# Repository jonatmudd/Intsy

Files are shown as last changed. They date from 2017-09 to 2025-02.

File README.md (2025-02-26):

# Intsy
32/64/128 channel bioamplifier system, now with accelerometer and on-board SD data logging capability for ambulatory applications! Photos of the original 32/64 channel device are below Also, check out the quick overview of the device internals and mechanical enclosure of the 128 channel ambulatory system in <a href =  "https://www.youtube.com/watch?v=RvYDtEdVOBU&feature=youtu.be">this video</a> (full credit to Riwaj Shrestha, Suyash Mathema, and Jeremy Wharton!).

Intsy is a validated, low-cost, open-source, wireless-enabled bioamplifier system.  The system can be configured for 32, 64, or 128 channel operation.  It has been validated for acquiring high-quality gastrointesinal slow wave and surface EMG electrical signals.  For more details, see our <a href =  "http://iopscience.iop.org/article/10.1088/1361-6579/aaad51">published peer-reviewed article in Physiological Measurement</a>. We have also regularly used Intsy to make <a href = "https://ieeexplore.ieee.org/abstract/document/8839813"> body surface recordings of colonic motilty patterns</a> using  conventiona wet (gel) as well as dry electrodes (see <a  href = "https://link.springer.com/article/10.1007/s10439-023-03137-w"> this journal article  </a>) 

Data can be streamed either in wired configuration over USB or wirelessly via bluetooth.  A LabView GUI allows for real-time visualization and saving to hard disk for off-line analysis.  Data rates of 32 chan x 110 Hz can be stably transmitted over bluetooth.  The USB wired configuration can achieve up to 2 kHz x 128 chan.  Matlab functions for converting binary Intsy data files into matlab format are provided.

The name Intsy comes from the two core components: Intan RHD2132 bioamplifier chip + Teensy 3.6 microcontroller.

Please see "Intsy_Setup_Guide.pdf" for detailed instructions on how to set up the 32/64 channel Intsy system. Assembly time is typically about 4 hrs.  Total cost is about $1500 for the 32 channel system,  $2400 for the 64 channel system, and $6000 for the 128 channel system (the dominant cost being the Intan RHD2132 amplifier boards).  That means  you can build your very own high-quality, low-cost, portable bioamplifier system in just a single afternoon!

All feedback and suggestions are warmly welcomed. 

<p align="center">
  
</p>
Above: Intsy 128 channel electronics and mechanical enclosure (circa May 2020)

<p align="center">
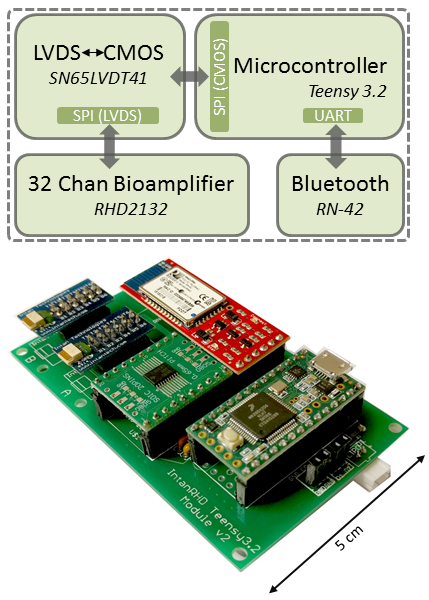
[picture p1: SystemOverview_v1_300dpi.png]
  
</p>
Above: Intsy hardware architecture and device (32/64 channel original module circa Dec 2017)

<p align="center">
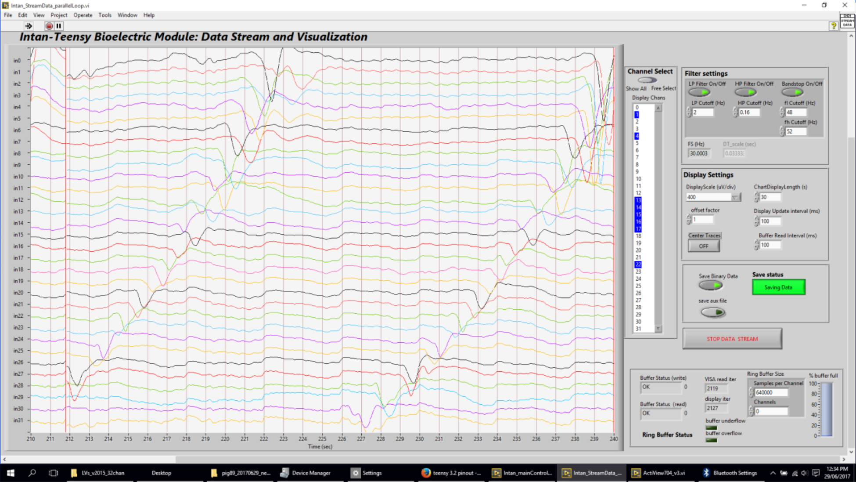
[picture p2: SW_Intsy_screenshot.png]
  
</p>
Above: Screenshot of Intsy Labview front end to visualize and stream signals in real time. The figure shows propagating gastric slow waves.

<p><font size="16"><b>Disclaimer</b></font></p>
The Intsy electronics module is not a medical device nor is it intended for medical diagnosis and provided to you "as is," and we make no express or implied warranties whatsoever with respect to its functionality, operability, or use, including, without limitation, any implied warranties, fitness for a particular purpose, or infringement. We expressly disclaim any liability whatsoever for any direct, indirect, consequential, incidental or special damages, including, without limitation, lost revenues, lost profits, losses resulting from business interruption or loss of data, regardless of the form of action or legal theory under which the liability may be asserted, even if advised of the possibility of such damages. This bioamplifier module does not fall within the scope of the European Union directives regarding electromagnetic compatibility, restricted substances (RoHS), recycling (WEEE), FCC, CE or UL, and therefore may not meet the technical requirements of these directives or other related directives

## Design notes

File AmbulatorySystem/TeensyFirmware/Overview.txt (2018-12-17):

Here you will find firmware for Teensy 3.6.  Compile and upload to Teensy 3.6 board using Arduino IDE
The main file is Intan_ambulatory_20181216.ino.  Opening it in Arduino should open a bunch of tabs with other .ino and .h files
Note: you will also need Bill Greimans' sdfat library before compiling: https://github.com/greiman/SdFat

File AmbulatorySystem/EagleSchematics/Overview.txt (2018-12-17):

Here you will find eagle schematics for the ambulatory board. Gerber files are included. Components mount on front and back
I used 4pcb (Advanced Circuits) to fab my boards.  Seeed studio is another good option I have used before.

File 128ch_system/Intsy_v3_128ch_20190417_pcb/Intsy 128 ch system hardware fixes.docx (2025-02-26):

Intsy 128 ch system hardware fixes. – Compiled 07 July 2019 JE

The system is verified complete and working as of June 2019. However, several fixes had to be made to schematic/board:

1. BT power switch. Connect/solder bridge the 2 pins on the ground line. This ensures BT ground pin and system ground supplied by Teensy are *always* connected. This prevents floating voltages from causing spurious signals in Rx/Tx lines which are always connected between BT and Teensy 3.6.
2. CS pin name/numbers are swapped. This problem is easily sorted by configuring firmware with proper numbers, but better is to fix CS A/B and CS C/D naming convention. They are inadvertently swapped in schematic moving from Intan RHD2000 across the LVDS converter to Teensy.

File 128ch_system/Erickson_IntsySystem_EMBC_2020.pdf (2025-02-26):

## Open-source 128-channel bioamplifier module for ambulatory monitoring of gastrointestinal electrical activity

Jonathan C. Erickson∗
, Beth Reed, Jeremy Wharton, Utkrist Thapa, Jack Robey, and Riwaj Shrestha

Abstract— We present an open-source, low-cost, portable, 128-channel bioamplifier module designed specifically for ambulatory, long-term (≥24 hr) monitoring of gastrointestinal (GI) electrical activity. The electronics hardware integrates stateof-the-art, commercial-off-the-shelf components on a custom PCB. Features include on-board data logging, wireless data streaming, subject motion monitoring, and stable operation up to the maximum 2 kHz/channel sampling rate tested. The new device operates for ≈ 30 hr continuously powered by a single

### 3.7 V, 2500 mAh LiPo battery. The 3D-printed ABS mechanical

enclosure is robust and small (13.1 × 8.8 × 2.5 cm), so that the device can be carried in a standard Holter monitor pouch. Results from initial 128-channel, high spatial resolution body surface colon mapping experiments demonstrate the utility of this new device for GI applications. The new bioamplifier module could also be used for multichannel recording experiments in a variety of biomedical domains to study electrical activity patterns of the neuromuscular system (EMG), uterus (EHG), heart (ECG), and brain (EEG).

I. INTRODUCTION
Multichannel electrical recordings find widespread use in variety of biomedical domains to assess heart (ECG), brain (EEG), neuromuscular (EMG), and uterine (EHG) function. One rapidly growing application area is the gastrointestinal (GI) field. For example, multichannel recordings have recently been used in research and clinical diagnostic settings to map the propagation of gastric slow waves using a minimally invasive endoscopic device as well as a noninvasive cutaneous electrode array [1], [2]. Similarly, electrocolonography (EColG) was recently introduced for noninvasively identifying cyclic motor patterns in the distal colon using an array of skin-surface electrical recordings [3]. As these GI technologies continue to mature, their capability to identify meaningful physiological information may be improved and extended by making recordings with increased spatial density and/or area coverage over a longer multi-day (≥ 24 hr) monitoring period.
To this end, we have developed a novel low-cost, open source, portable device with 128 input channels and on-board data logging capability. The new device, coined “Intsy-128”, is a substantial upgrade over the 32/64-channel electronics module previously developed in our lab, which was validated for making high-quality GI signal recordings [3], [4]. Specific new and upgraded features include: the maximum channel count has been increased from 64 to 128 channels; on-board microSD card data logging has been added to enable ambulatory applications; an accelerometer plus a flex

∗ Corresponding author: ericksonj@wlu.edu. The authors are with the Department of Physics and Engineering, Washington and Lee University, Lexington, VA 24450 USA.

sensor have been added to monitor participant movement; and a more powerful microcontroller has been integrated to support higher sampling rates. Additionally, we developed a small footprint, robust, custom 3D-printed ABS enclosure for the electronics board, which makes the new Intsy-128 device well suited for portable, ambulatory applications. The remainder of this paper details the electronic and mechanical design of the new Intsy-128 module. Herein, we also demonstrate the utility of this device in the GI field through initial experiments mapping colonic cyclical motor patterns stimulated by food intake using recordings from a 128-channel body surface electrode array. While the Intsy-128 was developed specifically with GI applications in mind, it could also be used in multichannel recording applications to study cardiac, neural, musculoskeletal, and uterine electrical activity patterns (e.g. [5]).

II. MATERIALS AND METHODS

A. Electronics Hardware System Design
The Intsy-128 electronics hardware is comprised of six main components integrated on a custom PCB (Figure 1 a-b). These include: Teensy 3.6 microcontroller (PJRC; Sherwood, OR); four Intan RHD2132 amplifier boards (Intan Technologies; Los Angeles, CA), two Texas Instruments SN65LVDT41 LVDS-CMOS transceivers for SPI over LVDS; one ADXL335 3-axis accelerometer (Adafruit Industries; New York City, NY) and a RN-42 “SilverMate” Bluetooth modem (Sparkfun; Niwot, CO). The custom PCB was designed using the free version of Eagle PCB design software (version 9.4). The module can be easily assembled in about 4 hrs using basic through-hole and surface mount soldering techniques.
The Teensy 3.6 microcontroller was selected because it offers multiple SPI ports; a relatively fast and powerful CPU (180 MHz ARM Cortex-M4); and native microSD support via a 4-bit SDIO interface with a maximum 12 MB/s write speed. On-board data logging is required for ambulatory studies. Each of four Intan RHD2132 amplifier boards has 32 inputs for a total of 128. The amplifier boards are interfaced to two SPI ports on the Teensy 3.6. The TI SN65LVDT41 ICs are used to translate TTL/CMOS signals used by Teensy 3.6 to low-voltage differential signaling (LVDS) used by the Intan headstages.
The RN-42 wirelessly streams data to a host PC for real-time signal visualization and analysis. RTS/CTS flow control was enabled for robust data transfer. Additionally, the Teensy firmware configures the wireless data stream to transfer the maximum possible number of channels at full

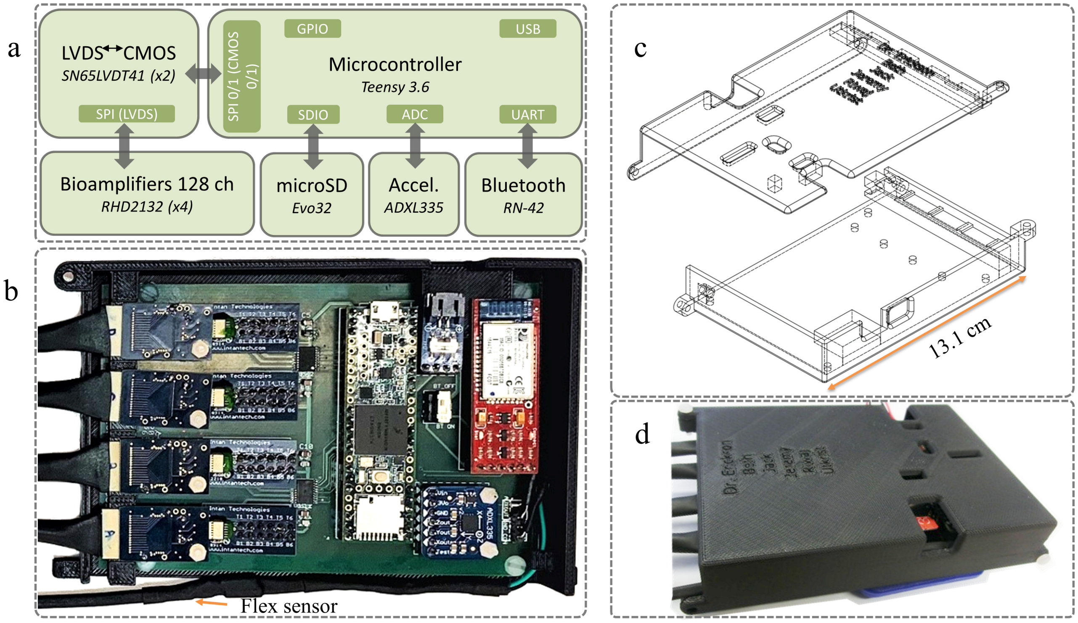
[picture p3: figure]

Fig. 1. System overview of the Intsy 128 device. a: Electronics design block diagram; b: Fully assembled PCB mounted in base of enclosure; c: 3-D CAD rendering of enclosure assembly showing base and lid. d: Fully assembled Intsy-128 module.

sampling rate without exceeding the total Bluetooth bandwidth. Alternatively, data may be streamed in real-time over
the USB port for higher bandwidth applications. Independent of data streaming, all data bytes are always logged on-board to a microSDHC UHS-I memory card (Samsung EVO Plus 32GB). Data logging write-speed was optimized by preallocating the data file and writing 512-byte (1-page) blocks to the microSD card data file. Each data frame consists of 270 bytes, including 256 bytes for electrical recordings (2-bytes for each of 128 amplifiers), 4-byte microsecond timestamp, and 10 bytes of “magic number” synchronization characters used to verify fidelity of SPI and SDIO interfaces.
The 3-axis accelerometer (ADXL335) and a custom flex sensor are used to measure subject motion during the study. The flex sensor is configured as a standard voltage divider comprised of a 47kΩ fixed resistor in series with a approx 20-400kΩ flexible resistor (Sparkfun) and is powered by a 3.3 V digital output pin on the Teensy 3.6. The accelerometer readings could be used for analysis of multi-day ambulatory monitoring applications [6]. Similarly, the flex sensor is more sensitive to subtle motions, such as bending or twisting of the abdomen, and may be used in the future to improve automated artifact reduction techniques [7].
The Insty-128 module is powered by a 3.7 V, 2500 mAh LiPo flat pack battery with an easily accessible switch to turn the device on or off. A separate power switch independently controls the Bluetooth module allowing users to save battery power when real-time wireless streaming is not required.

LED indicator lights on both the Bluetooth module and Teensy 3.6 serve as system status indicators.

B. 3D-Printed Enclosure

The electronics hardware module is secured inside a custom 3D-printed ABS enclosure case, which is durable and protects internal hardware from mechanical impacts experienced during an ambulatory subject experiment. The enclosure consists of a base and lid (Figure 1c). Seven nylon nuts and bolts secure the PCB circuit board and the lid onto the base of the case providing quick and efficient assembly (Figure 1d).
A wide-tooth “comb” pattern of indentations (15 mm wide with 2.5 mm gaps) was carefully incorporated into the base and lid to secure the connection between the electrodes and the amplifiers. Additionally, multiple ports are provided for viewing status-indicator LEDs, toggling power switches, and conveniently accessing the microSD card and USB port. The design focused on making a light and slim device conducive for ambulatory studies. The case dimensions are 13.1 × 8.8 × 2.5 cm, approximately the same size as a typical Holter cardiac monitor; thus, it can be easily carried in a Holter monitor pouch. The Intsy-128 module weighs a total of 216 grams, including the the fully-assembled PCB, ABS enclosure, and LiPo battery mounted externally on the enclosure’s base in a vinyl cell phone wallet pouch.

C. Software User Interface
A user-friendly custom suite of software built in Labview 2017 (National Instruments; Austin, TX) was used for device configuration and visualizing signals in real-time. This interface allows the user to configure the sampling rate, band-pass filter cutoffs for the Intan RHD2132, and SD card log file name. The LabView interface is also used to configure and optionally apply digital filters, as well as select a subset of channels, prior to display.
A file reader utility developed in Matlab 2019a (The Mathworks Inc; Nattick, MA) was used to import and convert the raw binary data files into physical values for further analysis. Firmware for the Teensy 3.6 was programmed using Teensyduino [8] in the Arduino IDE. All custom software, PCB and CAD design files are freely available and fully open-source [9].
D. Meal-response experiment
To demonstrate the utility of the Intsy-128 device, we performed initial body surface colon mapping experiments with n = 5 human subjects, following the protocol described in [3]. This study was approved by the Institutional Review Board of Washington and Lee University. In this study, we placed a 128-channel electrode array on the lower abdomen toward lower subject’s left side, approximately covering the sigmoid and descending colon. The 128-channel array was formed using two 64-channel (8 × 8) grids with 10 mm spacing (OTbioelettronica; Torina, Italy). We recorded signals for ≈90 min in the fasted state, and another 90 min in the fed state. The sampling rate was set to 100 Hz. Colonic signal analysis was based on the Continuous Wavelet Transform (CWT) [3]. Additionally, we quantified the acceleration magnitude as: A =

q
a

2
x + a

2
y + a

2
z

III. RESULTS

A. Hardware Performance Benchmark
Data logging was accurate and robust; zero errors were observed during approximately 60 hours of hardware validation experiments. The device remains stable at sampling rates up to 2000 Hz, the highest sampling frequency tested. The total current draw was measured be ≈100 mA; the LiPo battery continuously powered the module for ≈ 30 hr before it needed to be recharged. Users reported the device was unobtrusive and comfortable to wear over the duration of a 3-4 hr study.
B. Proof of Concept GI recordings
The Intsy-128 device made high-quality recordings of bioelectric activity. Figure 2 illustrates representative results for the body surface colon mapping experiments from one test subject. We visually assessed the ECG waveform (digitally high-pass filtered, 1 Hz cutoff) with the QRS complex and T-wave clearly visible as a proxy indicator for good-quality, low impedance electrode-skin contact (Fig. 2a). The EColG time-domain signal (digitally band-pass filtered, 0.5-10 cpm) indicates a clear increase in colonic activity at a dominant frequency of 3.2 cylces per minute (cpm) in the fed vs. the fasted state (Fig. 2b). CWT spectral analysis shows the time-course of increased colonic activity following meal-ingestion (Fig. 2c). Note that the time-course of increased subject motion during eating (acceleration A low-pass filtered at 1 Hz, gray trace), does not explain a proportionally much larger rise in post-meal colonic activity (Fig. 2d). The time-course of increased post-meal colonic activity beginning about 12 min after eating and lasting for about 30 min is strongly concordant with the cyclic motor activity in the distal colon previously characterized [3], [10]. Fig. 2e shows the 128-channel electrode array placed on the lower abdominal surface below umbilicus (overhead view). The flex sensor is visible as finger-like projection on the left-side of the photo (subject’s right). The overlaid black curves indicate the approximate location and orientation of a segment of the colon identified from body surface mapping localization. The body surface heat map computed from the power-percent difference in pre- vs. post-meal activity [3] localizes the active colonic regions to the infraumbilical region, toward the left iliac crest (Fig. 2f). The velocity field map (Fig. 2g) was derived using the surface Laplacian and phase-based analysis
[11] indicates retrograde wave activity originating near the rectosigmoid region propagating at of 5.3 ± 2.0 mm/s (mean ± s.d.), in reasonable accord with findings from previous high-resolution manometry studies [10].

IV. DISCUSSION

A. Comparison to other modules
The new Intsy-128 device is a low cost, open-source, easy to assemble bioamplifier module well-suited for ambulatory bioelectrical signal acquisition and analysis. Table I compares Intsy-128 to similar and academically-sourced and open-sourced hardware. Intsy-128 offers the highest channel count and sampling frequency compared to other devices in its class. The on-board data logging capability and motion monitoring make it especially well-suited for ambulatory studies. The Intsy-128 may be an attractive option for budget-conscious labs, fostering new discovery and innovation throughout the scientific community.
| Intsy-128 | Ref [12] | OpenBCI [13]
Number channels | 128 | 64 | 16
Resolution (bits, µV/bit) | 16, 0.195 | 10, 1.56 | 24, 0.006
Dynamic Range (mV) | ±5 | ±3 | ±104
Analog filter | 0.02 Hz-5kHz | 0.016-1.6 Hz | no filter
Max Sampling Rate (kS/s) | 256 | 64 | 16
Validation in vivo | Yes | No | Yes
Cost/channel (USD) | 35 | unknown | 59

TABLE I

COMPARISON OF AMBULATORY-READY SYSTEMS.

B. Potential applications and future work
In the future, the size and cost of the Intsy-128 module could be optimized by combining all individual components on a single custom PCB using all surface mount assembly, as opposed to mounting relatively large submodules with through-hole soldering. The addition of WiFi capability would allow for higher bandwidth streaming, which is important for applications with much higher sampling frequencies (≥ 500 Hz), as are typical in the neural and cardiac fields.
V. CONCLUSIONS
We have developed a novel low-cost, open-source, 128-channel bioamplifier module, suitable for ambulatory studies. Results from ≈3 hr colonic meal response study conducted in a laboratory setting demonstrate its potential use in high-resolution mapping studies of GI electrical activity patterns. In the future, it can also be used for longer-term monitoring and diagnostic studies. The Intsy-128 bioamplifier module could also be used to study electrical activity patterns of the brain, heart, skeletal muscle, and uterus.

VI. ACKNOWLEDGMENT
This work was supported by the Washington and Lee University Lenfest Faculty Research Grant (JCE); Advanced Immersion and Mentoring Program (JW); Allen Research Grant (JR); and Summer Research Scholars Program (UT and RS).

REFERENCES

[1] T. Angeli et al., “High-resolution electrical mapping of porcine gastric slow-wave propagation from the mucosal surface,” Neurogastroenterology & Motility, vol. 29, no. 5, 2017.
[2] A. A. Gharibans et al., “Spatial patterns from high-resolution electrogastrography correlate with severity of symptoms in patients with functional dyspepsia and gastroparesis,” Clinical Gastroenterology and Hepatology, 2019.
[3] J. C. Erickson et al., “Electrocolonography: Non-invasive detection of colonic cyclic motor activity from multielectrode body surface recordings,” IEEE Transactions on Biomedical Engineering, 2019.
[4] ——, “Intsy: a low-cost, open-source, wireless multi-channel bioamplifier system,” Physiological measurement, vol. 39, no. 3, p. 035008, 2018.
[5] C. Rabotti and M. Mischi, “Propagation of electrical activity in uterine muscle during pregnancy: a review,” Acta Physiologica, vol. 213, no. 2, pp. 406–416, 2015.
[6] N. Paskaranandavadivel et al., “Multi-day, multi-sensor ambulatory monitoring of gastric electrical activity,” Physiological measurement, vol. 40, no. 2, p. 025011, 2019.
[7] A. A. Gharibans et al., “Artifact rejection methodology enables continuous, noninvasive measurement of gastric myoelectric activity in ambulatory subjects,” Scientific reports, vol. 8, no. 1, p. 5019, 2018.
[8] P. Stoffregen, “Teensyduino: a software add-on for the arduino,” https: //www.pjrc.com/teensy/teensyduino.html, accessed: 2020-01-25.
[9] “Github: Intsy 128-channel ambulatory bioamplifier system,” https://github.com/jonatmudd/Intsy/tree/master/AmbulatorySystem, accessed: 2020-01-30.
[10] P. Dinning et al., “Quantification of in vivo colonic motor patterns in healthy humans before and after a meal revealed by high-resolution fiber-optic manometry,” Neurogastroenterology & Motility, vol. 26, no. 10, pp. 1443–1457, 2014.
[11] A. A. Gharibans et al., “High-resolution electrogastrogram: A novel, noninvasive method for determining gastric slow-wave direction and speed,” IEEE Transactions on Biomedical Engineering, vol. 64, no. 4, pp. 807–815, 2017.
[12] A. Javan-Khoshkholgh and A. Farajidavar, “An implantable inductive near-field communication system with 64 channels for acquisition of gastrointestinal bioelectrical activity,” Sensors, vol. 19, no. 12, p. 2810, 2019.
[13] “OpenBCI,” https://shop.openbci.com/collections/frontpage/products/cyton-biosensing-board-8-channel?variant=38958638542, (https://shop.openbci.com/collections/frontpage/products/cyton-biosensing-board-8-channel?variant=38958638542) accessed: 2020-01-20.

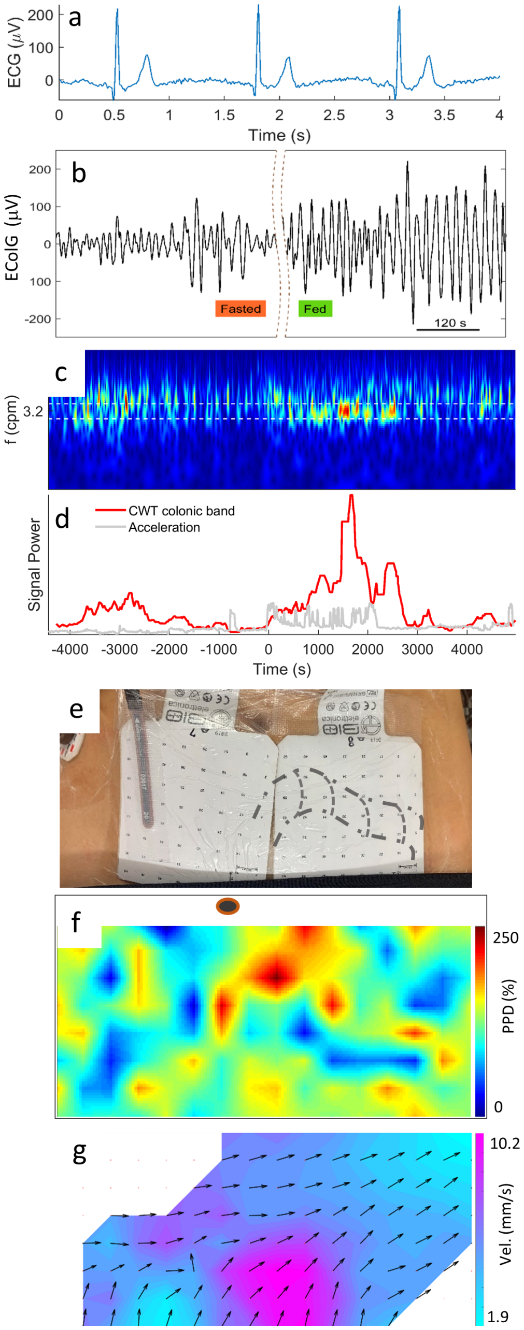
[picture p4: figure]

Fig. 2. EColG meal-response experiment representative results. a: ECG waveform. b: EColG signals in fasted and fed state; note the “broken” time axis. c, d: CWT analysis showing strong post-meal activity with a dominant frequency of 3.2 cpm; e: Photo of electrode array positioned on lower abdomen spanning subject’s midline; f: Heat map localizing colonic post-meal activity. Brown circle denotes belly button position; g: Velocity field map indicating a retrograde motor pattern.

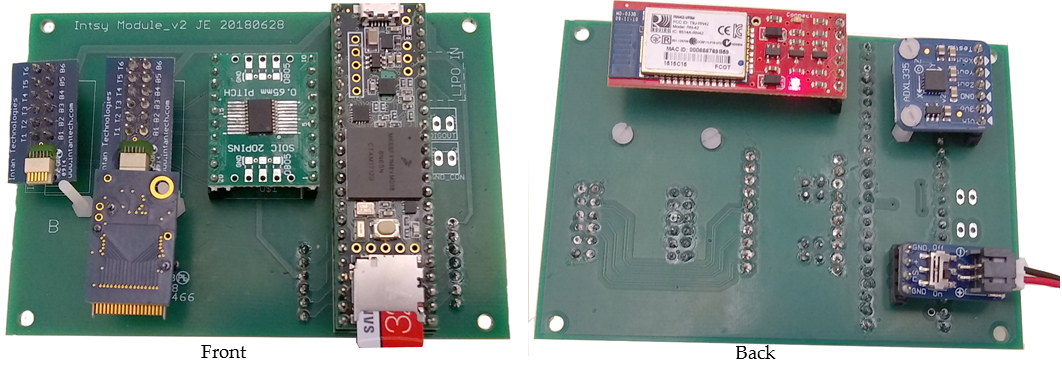
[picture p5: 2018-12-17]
IntsyAmbulatoryFrontBack_cropped_new.png

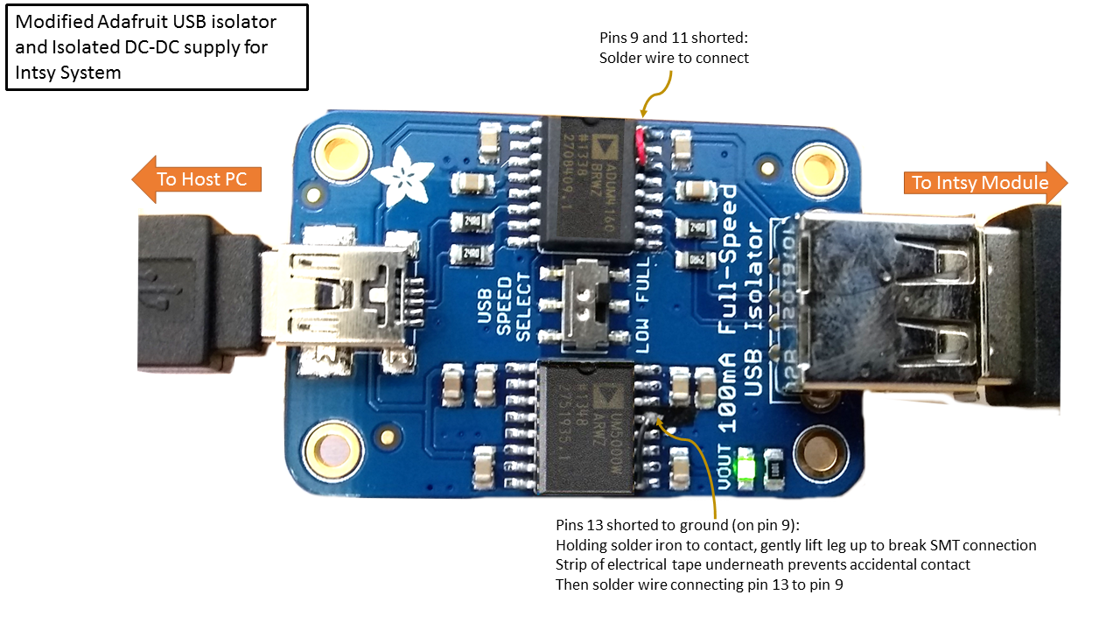
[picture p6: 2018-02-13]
USBisolator_modififcation.png

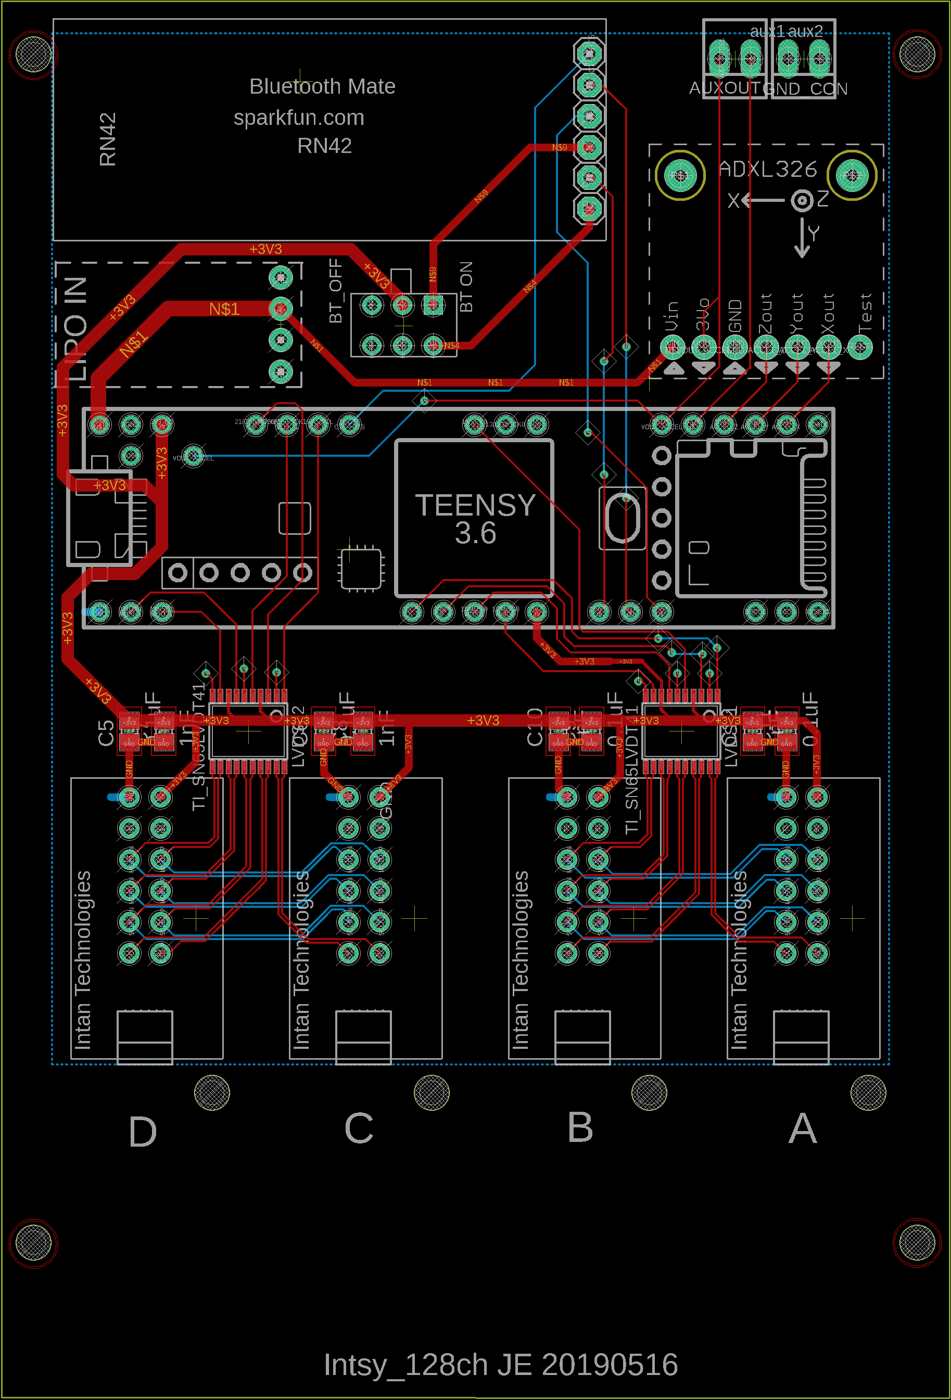
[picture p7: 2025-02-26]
128ch_system/Intsy_v3_128ch_20190417_pcb/Intsy_128ch_highRes.png

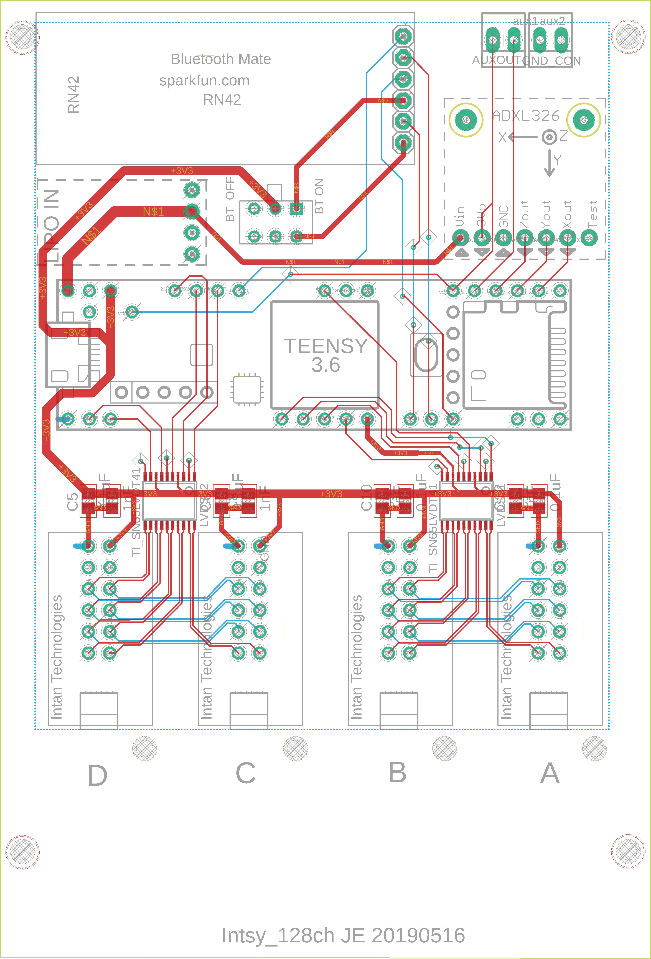
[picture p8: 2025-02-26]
128ch_system/Intsy_v3_128ch_20190417_pcb/Intsy_128ch_1200dpi.png

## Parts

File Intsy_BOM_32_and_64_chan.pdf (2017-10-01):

1

I. BILL OF MATERIALS

TABLE I

BILL OF MATERIALS FOR INTSY BIOAMPLIFIER MODULE. PRICES DO

NOT INCLUDE TAX OR SHIPPING.

Item | Vendor (part #) | Cost (USD)
RHD2132 amplifier board | Intan Tech (C3314) | 895 per 32 chan amp board
SPI cable adapter board | Intan Tech (C3430) | 98 per amp board
36 pin electrode adapter board | Intan Tech (C3420) | 190 per amp board
Teensy 3.2 microcontroller | Adafruit (2756) | 20
RN-42 Bluetooth module Silver mate | Sparkfun (WRL-12576) | 25
TI LVDS-CMOS driver/receiver SN65LVDT41 | Mouser (595-SN65LVDT41PW) | 8
Schmartboard 0.65mm SOIC to DIP adapter | Mouser (872-204-0006-01) | 6
Male and Female 0.1” pitch headers | Adafruit (3009; 3008) | 5
Bypass capacitors, 2 x 0.1 uF, 2 x 1 nF | Mouser (80-C320C104K5R; 75-
| 564R60GAD10) | 1
JST LiPo battery connector | Sparkfun (PRT-08613) | 1
LiPO battery (3.7 V; 1200 mAh) | Adafruit (258) | 10
USB isolator | Adafruit (2107) | 35
Custom PCB | Seeed Studio | 10
TOTAL | | 1304 (32 chan)/2487 (64 chan)

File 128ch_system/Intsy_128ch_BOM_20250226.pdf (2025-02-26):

## Intsy 128 channel bioamplifier module: Bill of Materials

(compiled Jon Erickson Feb 26 2025)

Item | Vendor (part #) | Unit Cost (USD) | Quantity (for 128 ch)
RHD2132 headstage | Intan Tech (C3314) (https://intantech.com/RHD_headstages.html?tabSelect=RHD32ch) | 920 | 4
SPI cable adapter board | Intan Tech (C3430) (https://intantech.com/RHD_SPI_cables.html?tabSelect=RHDSPIadapter) | 111 | 4
36 pin-wire adapter | Intan Tech (C3420) (https://intantech.com/electrode_adapters.html?tabSelect=Wire36pin) | 230 | 4
Teensy 3.6 microcontroller | N/A ¹ | 20 | 1
TI LVDS-CMOS driver receiver SN65LVDT41PW | Mouser (595-SN65LVDT41PW) (https://nz.mouser.com/ProductDetail/Texas-Instruments/SN65LVDT41PW?qs=QViXGNcIEAu2oZm1OztEtQ%3D%3D) | 18 | 2
RN-42 Bluetooth module Silver mate | Sparkfun² (retired part) (https://learn.sparkfun.com/tutorials/using-the-bluesmirf/hardware-overview) | 25 | 1
ADXL335 analog 3-axis accelerometer | Adafruit (163) (https://www.adafruit.com/product/163) | 15 | 1
JST switch | Adafruit (1863) (https://www.adafruit.com/product/1863) | 3 | 1
Bypass caps: 0.1 uF; 1 nF | Mouser (80-C320C104K5R; 75-564R60GAD10) | 4 (of each value) | 1
USB isolator | Adafruit (2107) (https://www.adafruit.com/product/2107) | 35 | 1
LiPo battery (3.7 V; 2500 mAh) ³ | Adafruit (328) (https://www.adafruit.com/product/328) | 15 | 1
Custom PCB | Seeed Studio or Advanced Circuits | 10 | 1
3D printed enclosure | Local 3D printer | ~20 | 1
Nylon screws and nuts (various sizes, eg M2) | McMaster-Carr | 5 | various
Snap leads (0.5 m, 10x pack) ⁴ | OpenBCI (snap leads) (https://shop.openbci.com/products/emg-ecg-snap-electrode-cables?variant=46183825277168) | ~ 600 | 13 packs

1

Teensy 3.6 is now deprecated and common vendors (Digikey, Mouser, Adafruit, Sparkfun, PJRC) appear to be out of stock. If a Teensy 3.6 cannot be procured, one alternative is to use a Teensy 4.1 (blazing fast!). Note: T4.1 is not a drop-in replacement (not pin-for-pin compatible), therefore the pcb files must be updated accordingly!

2 RN-42 Bluetooth silver mate module is now ‘retired’ by sparkfun. Suggested workarounds: 1) Use the Intsy module in wired mode only. In this case, the Bluetooth module is not required and may be entirely left off the board. 2) the RN-42 bluetooth component is still available from various vendors. Buy one of these, then download and fabricate one of sparkfun’s original pcbs for the silver mate module.

3

LiPo battery with 2500 mAh battery should be sufficient for running the Intsy module for approximately ~ 16 hr ( = 2500 mAh/150 mA = 50/3 hr). WARNING: only a single power source may be safely applied to the Intsy module. The LiPo battery and USB cord should should NEVER be plugged in at the same time!

4 Any snap leads will do. OpenBCI offers one relatively inexpensive option. However, in my hands, some of the clips are cheaply made and fail (probably 1 out of 20).

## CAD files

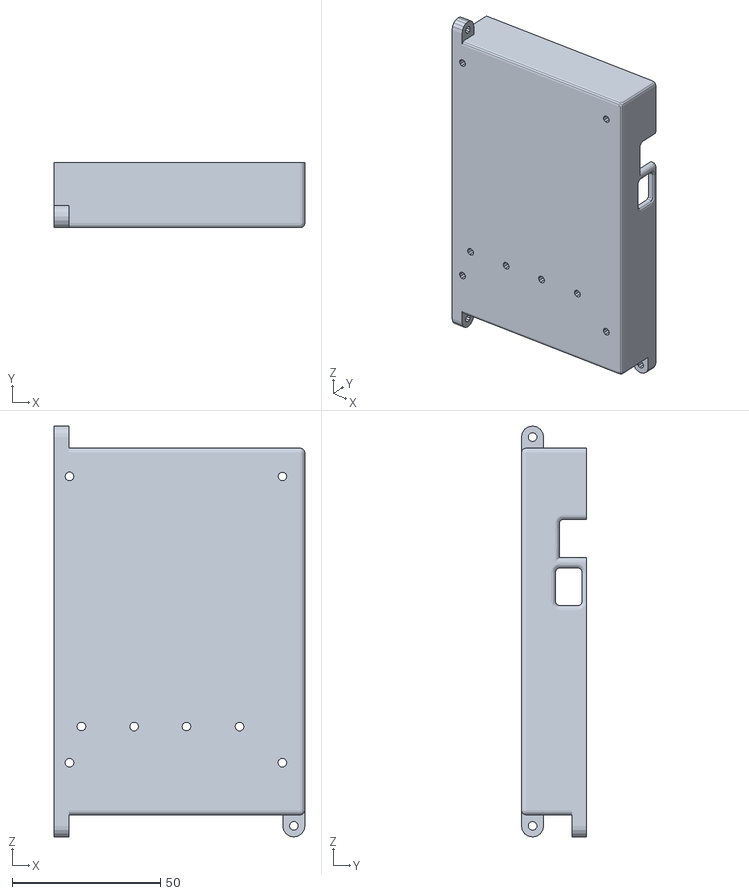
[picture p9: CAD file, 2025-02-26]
128ch_system/Box_128Chan_3dprint/ENGN_128chan_box_4.stl
84.8 x 22.0 x 138.8

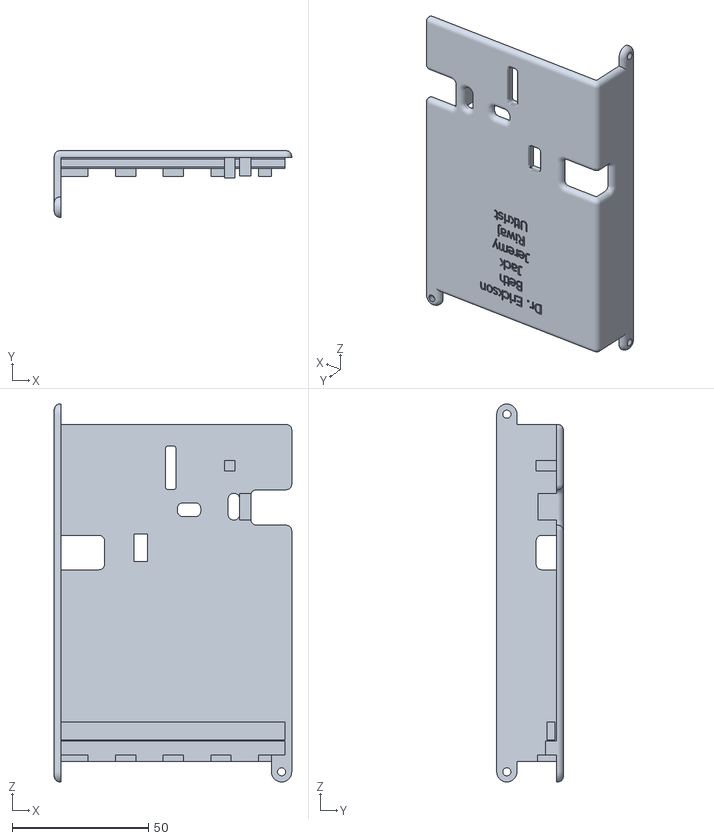
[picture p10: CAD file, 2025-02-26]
128ch_system/Box_128Chan_3dprint/ENGN_128chan_lid_4.stl
87.3 x 24.5 x 138.8

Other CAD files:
128ch_system/Box_128Chan_3dprint/128chan_box_Botton half Drawing.dwg
128ch_system/Box_128Chan_3dprint/128chan_lid.dwg
128ch_system/Box_128Chan_3dprint/128chan_box_2_FixedMeasurements.ipt

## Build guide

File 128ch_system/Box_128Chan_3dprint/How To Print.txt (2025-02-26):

0) If the latest version of the box or lid has been modified,
	it will have to be exported as an STL and the previous STL file
	should either be deleted or placed in the OldVersions folder.
	The STL file should be prefixed with 'ENGN_'.

1) Open the 3d slicer program on a computer in the IQ Center.

2) Drag both the box and lid STL files into the slicer and print.

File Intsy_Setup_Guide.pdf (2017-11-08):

### Intsy Hardware Module Assembly

Below are assembly instructions for the Intsy hardware module. Assembly requires only basic soldering skills. Anyone with modest experience can do it! Total assembly time is typically about 2-4 hours. The fully assembled module is shown in Figure 1.

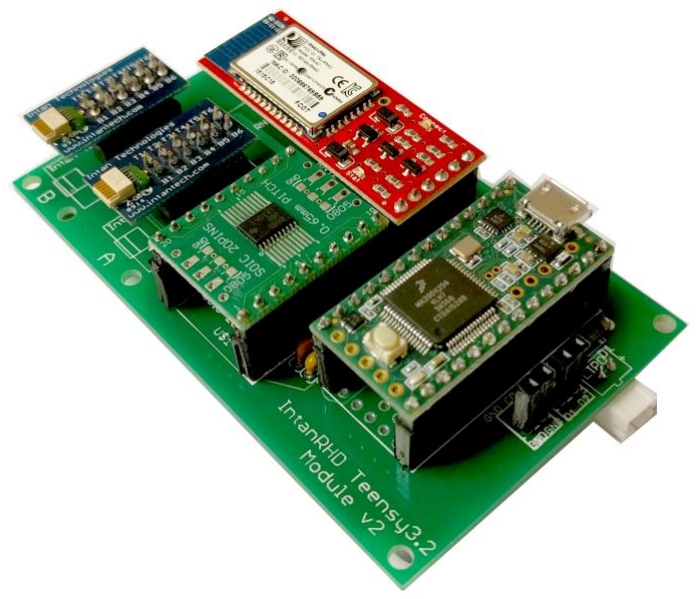
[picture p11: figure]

Figure 1. Assembled Intsy PCB. Battery connection and Intan RHD2132 amplifiers not shown.

Tools you’ll need
- Soldering iron and solder + flux.
- Box knife of ultrasonic blade to cut rectangular headers to size
- Tweezers and/or needle nose pliers

Solder PCB headers and components
1. Solder power by-pass capacitors into board (yellow blobs in Figure 2). Be careful to properly orient electrolytic capacitors, if used. The positive side (longer leg) should connect pins 4 and 8 of the TI LVDT41 chip. These are easily identified as connecting to the thick, light green power rail.
2. Insert Schottky polarity protection diode as shown in Figure 2. The cathode (gray stripe) must be oriented toward the top right corner of the board.
Step 1b: Solder female rectangular headers on top side of PCB. Two-row headers may be convenient for the Intan RHD2132 adapter slots. Otherwise, use single row headers cut to the proper number of contacts. Make sure they remain vertical during soldering; it is recommended to secure pieces with masking tape prior to soldering.

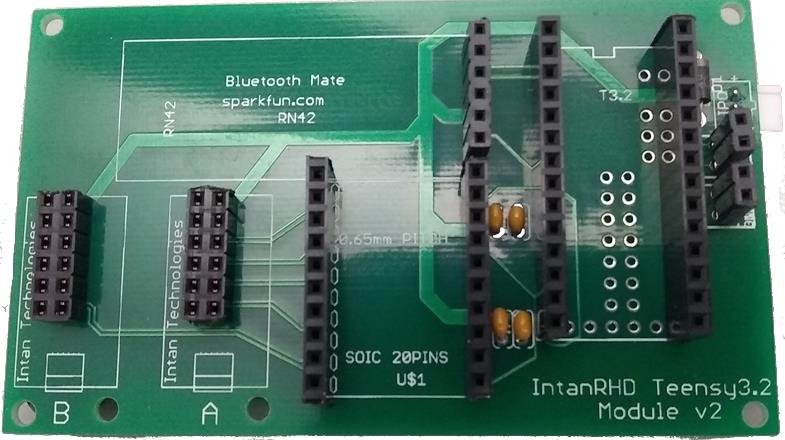
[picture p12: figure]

Figure 2. PCB top side

4. Flip the board over, solder and solder in the JST LiPo battery connector (Figure 3). The mechanical strength of the solder is weak, so it is recommended to add a drop of epoxy or hot glue to secure the element to the PCB.
5. Optionally add adhesive bumper feet to the corner of the board. Bumper feet reduce slipping. They also reduce the risk of conductive elements shorting out if Intsy is placed on a metal table or other conductive surface.

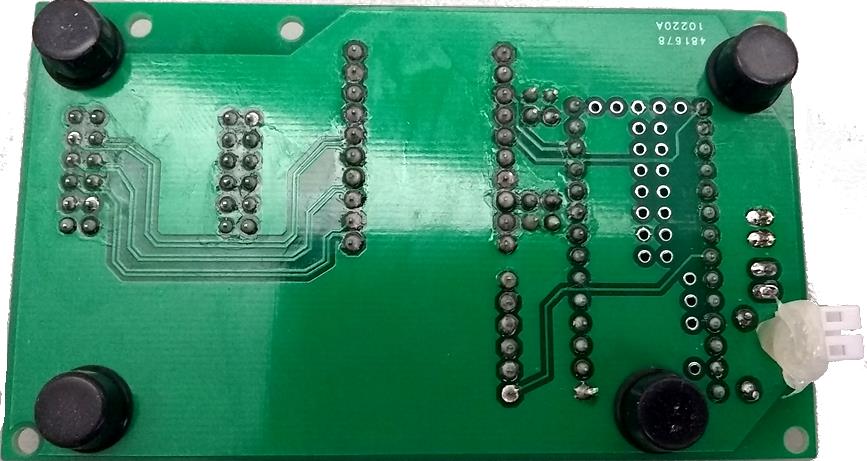
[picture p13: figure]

Figure 3. PCB bottom side.

Prepare commercial off-the-shelf components
1. Solder male header pins into the Schmartboard SOIC to DIP adapter. It is recommended to place the male pins in a standard breadboard, then the Schmartboard on top to ensure the pins remain vertical and flush to the board during soldering. Carefully place then surface mount solder the SN65LVDT41

LVDS-CMOS translator and tape it securely in place with masking tape of similar. Flux must be applied with a flux pen prior to soldering. The temperature of the soldering iron must be at least 800 F. Detailed instructions can be found here. (http://schmartboard.com/content/Other/schmartboard_dc_ez_instructions.pdf) The assembled LVDS component is shown in Figure 4.

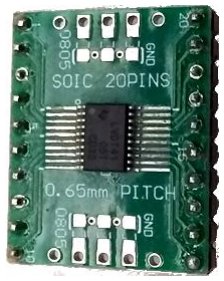
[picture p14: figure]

Figure 4. Schmartboard SOIC-DIP 20 pin adapter with mounted LVDS-CMOS translator (SN65LVDT41).

2. Solder male 0.1” pitch pins into the RN-42 Bluetooth Silver Mate module, into the Teensy 3.2 microcontroller (Figure 5). The same technique of placing pins in the breadboard to ensure vertical and flush mounting to the component should be used.

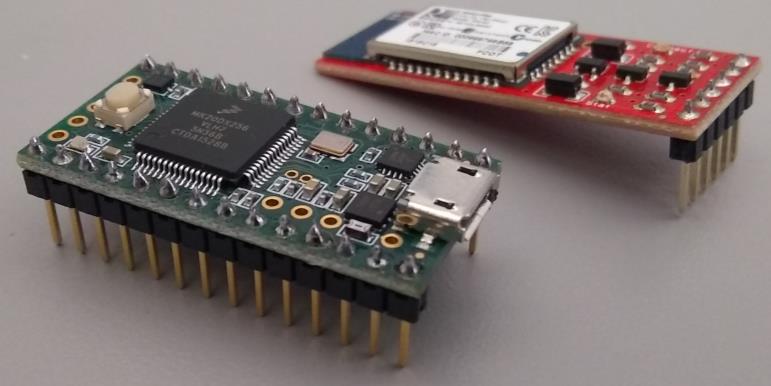
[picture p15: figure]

Figure 5. Teensy 3.2 and Sparkfun Bluetooth mate silver with male pins soldered in.

3. Solder dual-row male header pins into the Intan SPI cable adapter boards (see Figure 1, slots A and B)
4. Add the 100 MOhm external resistor to the RHD2132 board. The resistor should connect between pins labeled AUX3 and ground, as shown in Figure 6.

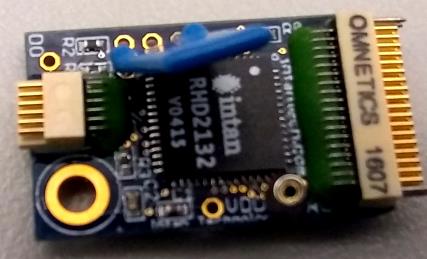
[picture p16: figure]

Figure 6. Intan RHD2132 ampliifer board, with external 100 MOhm resistor added (blue).

Mount components on PCB
1. Carefully plug in the Teensy 3.2, oriented as shown in Figure 1. The USB connector should face away from the “Intan RHD Teensy 3.2” text printed on the PCB.
2. Carefully plug in the Schmartboard SOIC-DIP adapter board. Make sure pin faces away from the RN-42 bluetooth module. The “SOIC 20PINS” text should be near the PCB edge.
3. Plug in the Intan SPI cable adapters as shown. The Omnetics connectors face outward.
4. Plug in the RN-42 Bluetooth module.

Connecting to amplifiers and host computer
1. It is now time to upload firmware to the Teensy 3.2. It is best to do this using a wired-USB connection (as opposed to over-the-air with Bluetooth). See the separate guide on programming the Teensy for specific instructions.
2. Decide if you are going to use wired or wireless mode. If using wireless mode, plug in a 3.7 V LiPo battery. If using wired mode, you can power the board directly from the USB port. However, it is strongly recommended to use a USB Isolator. See the separate guide on powering the Intsy module for further details.
3. Regardless of wired or wireless configuration, use a multi-meter to verify that 3.3 V is being delivered to all components. This is critically important for the Intan amplifiers which accept only 3.0 – 3.6 V. Anything higher, and you will instantly fry the Intan amplifiers!
4. Assuming power connections are verified to be ~ 3.3 V (absolutely no higher than 3.6 V), proceed…
5. Connect the Intan amplifier(s). These may be connected using a SPI cable from Intan. Alternatively, the Intan RHD2132 bioamplifiers may be directly connected to the board by ‘flipping over’ the amplifier to mate with the SPI cable adapter boards.

Congratulations - Your Intsy module is now fully assembled and ready to use! See, that was easy

### Intsy Power Supply

Created: Jon Erickson 11 May 2017
Modified: 07 Nov 2017

The Teensy 3.2 LDO voltage regulator LP38691 supplies “max 250 mA” continuous current. Dropout voltage is about 65 – 200 mV. In general, we can use the Teensy 3.2’s on-board voltage regulator to distribute power to all other module components: Intan RHD2000 amps (note 3.6V hard max!); RN42 Bluetooth; LVDS-CMOS converter. The 3.3V regulated output on the Teensy is be distributed to these components. Note that you can NOT substitute Teensy 3.1, which has different power-supply circuitry.

The power supply for the Insty system depends on the which configuration is implemented:

1) Wired configuration: Regulated input to V_USB, or unregulated input. We recommend using a modified Adafruit digital USB isolator + DC-DC converter (https://www.adafruit.com/product/2107) which supplies regulated 3.3V at Micro-AB-1 USB cable connection. Using the USB isolator is recommended to improve data quality (remove potential ground loop) and for test subject safety/electrical isolation from the mains.
a. The Adafruit must be modified for 3.3V operation, per instructions below.
2) Wireless configuration: 3.7 V LiPo battery connected to V_IN. This is also routed through Teensy’s on-board LDO, so we get a 3.3 V output at the 3.3V pin.

Intended usage is to use ONLY ONE power source at a time: either the USB cable OR the LiPO battery, but not both.

Modifying the Adafruit USB isolator
On the ADu4160 USB isolator IC, V_DD2 and V_Bus2 (pins 9 and 11) must be shorted to be compatible with 3.3 V logic. On the ADm5000 (dc-dc converter) V_SEL (pin 13) must be shorted to ground to output regulated 3.3 V. In order to do this, the leg of the ADm5000 IC must be lifted off of the PCB.

TEENSY 3.2 Schematic from PJRC website

Note the LP38691 LDO is driven by either VUSB or Vin. 3.3 V regulated output is available on multiple pins.

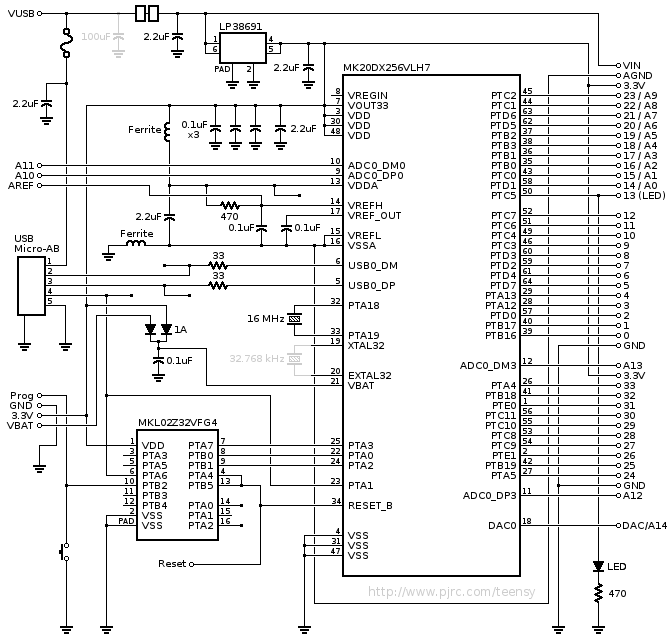
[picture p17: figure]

### Intsy Firmware and Front-End Software Installation: How to connect to a host PC

Jon Erickson
Created: 27 Feb 2017
Updated: 07 Nov 2017

Installing Teensyduino
1. Install Teensy Loader: https://www.pjrc.com/teensy/first_use.html
2. Install Teensyduino from PJRC: https://www.pjrc.com/teensy/td_download.html

Notes: On Windows 10, the Teensy is typically recognized as a USB HID device on first use. Teensy must appear as COM device in order to interface properly with LabView. The remedy is easy, just ‘verify’ a build for it in the Arduino IDE, then the device changes from USB HID to COM port. See this this thread, especially post #13 in the PJRC forums: https://forum.pjrc.com/threads/28726-newteensy-3-1-not-recognised-by-windows. (https://forum.pjrc.com/threads/28726-new-teensy-3-1-not-recognised-by-windows) Note the same “trick” works with the Teensy 3.2

Specifically, “Plug the fresh Teensy to a new USB port and wait for HID driver install, then [in Arduino IDE] hit program button after 'Verify' build. Then USB #40 showed up ready to go.”

3. Verify that firmware for controlling the Intan chip has been uploaded to the Teensy 3.2. Note there are currently 2 firmware libraries to choose from depending on whether you want to use the Intsy as a 32 or 64 channel module. The firmware you upload must match the channel count. The latest firmware versions, respectively, are contained in
TeensyFirmware_32chan or TeensyFirmware_64chan.
4. After selecting your version of firmware, open the main file, which is Intan_LV_interface_32chan.ino or Intan_LV_Interface_64chan_alpha.ino, for 32 or 64 channel modules, respectively.
5. Click the verify then the upload buttons in the Arduino IDE. Doing so should result in compiling and uploading the firmware the Teensy 3.2

Optional Bluetooth connection
1. Open Bluetooth Settings. Let Windows search for new device. The RN-42 module should be detected automatically (in this case as RNBT-9B59 or similar).
2. Identify the COM port number associated with the RN-42. In Windows 7, this is done by opening Bluetooth connections from the Control panel and right clicking to select Properties. In Windows 10, this can be done by scrolling to bottom of Bluetooth Devices > Click “More Bluetooth Options” > Click COM ports tab on Bluetooth Settings Windows that pops open. Look for the “Outgoing” direction COM port. Helpful post on this here.
3. If you are not using windows 10-- i.e., you are using Windows 7-- then you will need to use a USB Bluetooth dongle. (Prior to windows 10, no native Bluetooth API existed).
Almost any legitimate model should be recognized by most windows 7 and installed. Once the COM port has been identified, it is necessary to program the RN-42 to work in MDM SPP mode. This allows CTS/RTS flow control, essential for stable connections streaming data at a high rate.
a. Use CoolTerm or TeraTerm to establish a connection with the Bluetooth COM port.
b. Type X to see all settings. The RN-42 should report back a range of settings. Check that the UART speed is set to 115k.
c. Update the profile to MDM SPP by typing S~,3.

d. For more details see page 29 of Roving Network’s manual: http://ww1.microchip.com/downloads/en/DeviceDoc/bluetooth_cr_UG-v1.0r.pdf And/or the sparkfun tutorial: https://learn.sparkfun.com/tutorials/using-thebluesmirf?_ga=1.59342189.1999315961.1476995915 (https://learn.sparkfun.com/tutorials/using-the-bluesmirf?_ga=1.59342189.1999315961.1476995915)

You are now ready to connect to the Intsy module!

Installing LabView library
1. Copy and extract LabView library folder to host machine. The most recent versions of 32 and 64 channel versions are currently in LabView32chan and LabView64chan.
2. Download a copy of NI’s software circular buffer library: http://www.ni.com/tutorial/7188/en/
3. Install the software circular buffer module in <root>/LVs/swcircularbuffer1.0.19/setup.exe
4. Open <root>/LVs/Intan_mainControlPanel.vi. The first time loading on a new machine, this may take a minute, as labview is locating and compiling all of the modules.
5. Identify the Teensy COM port number in Windows Device Manager. Select it in under “VISA resource name” in Intan_mainControlPanel.vi. Select the corresponding COM port type (either USB serial or Bluetooth).
6. Configure all other hardware settings and save file settings.
a. All registers must be configured upon Intan power up.
b. Following the initial configuration, configuring reg 0-7 and 14-17 (Apwr) is optional, but recommended.
c. Hardware filter settings and sampling frequency may be updated independently.
7. Click the white Run arrow. This configures all selected registers with the chosen settings
8. The purple “Start Data Stream” button will become enabled, once Intan register configuration is complete. Click the purple button to start the data streaming. Doing so should open a new window in LV (Intan_streamData_parallelLoop.vi) with various filter controls etc.
9. The user can update all the visualization settings in real-time: LPF, HPF, BPF, channel selection, Y-scale, etc.
10. Saving the file may be discontinued within this window, but it is strongly recommended NOT to do so.

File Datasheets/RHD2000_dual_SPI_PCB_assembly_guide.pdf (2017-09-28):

## RHD2000 Dual SPI Board

2.0”

4.9”

ThinFlex PCB (0.005” ± 0.002”, 1 mil core, 1 oz. copper), ENIG gold immersion finish (2 μm)

No through-hole components; only three SMD connectors on top side only

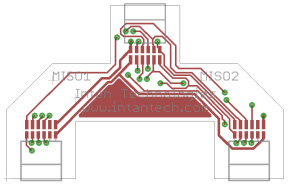
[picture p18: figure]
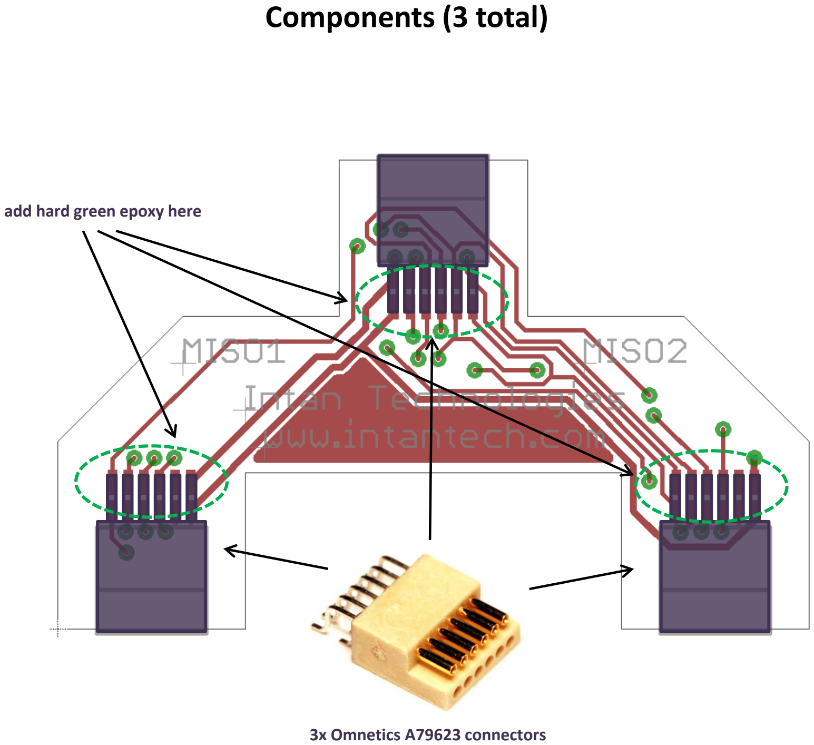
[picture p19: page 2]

Components (3 total)

3x Omnetics A79623 connectors

add hard green epoxy here

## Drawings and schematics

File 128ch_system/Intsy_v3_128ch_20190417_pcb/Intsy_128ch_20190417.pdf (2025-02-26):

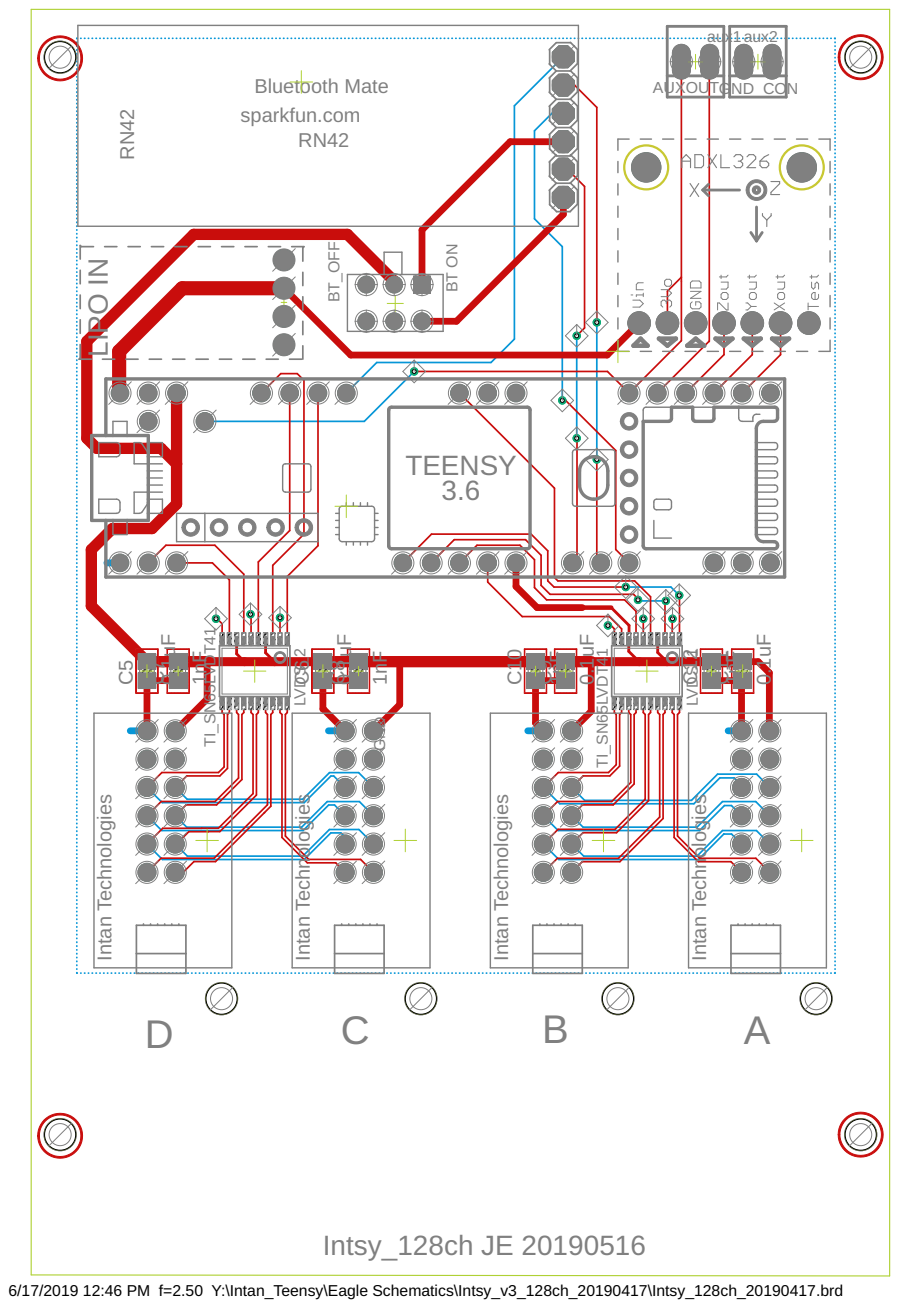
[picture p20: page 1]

6/17/2019 12:46 PM f=2.50 Y:\Intan_Teensy\Eagle Schematics\Intsy_v3_128ch_20190417\Intsy_128ch_20190417.brd

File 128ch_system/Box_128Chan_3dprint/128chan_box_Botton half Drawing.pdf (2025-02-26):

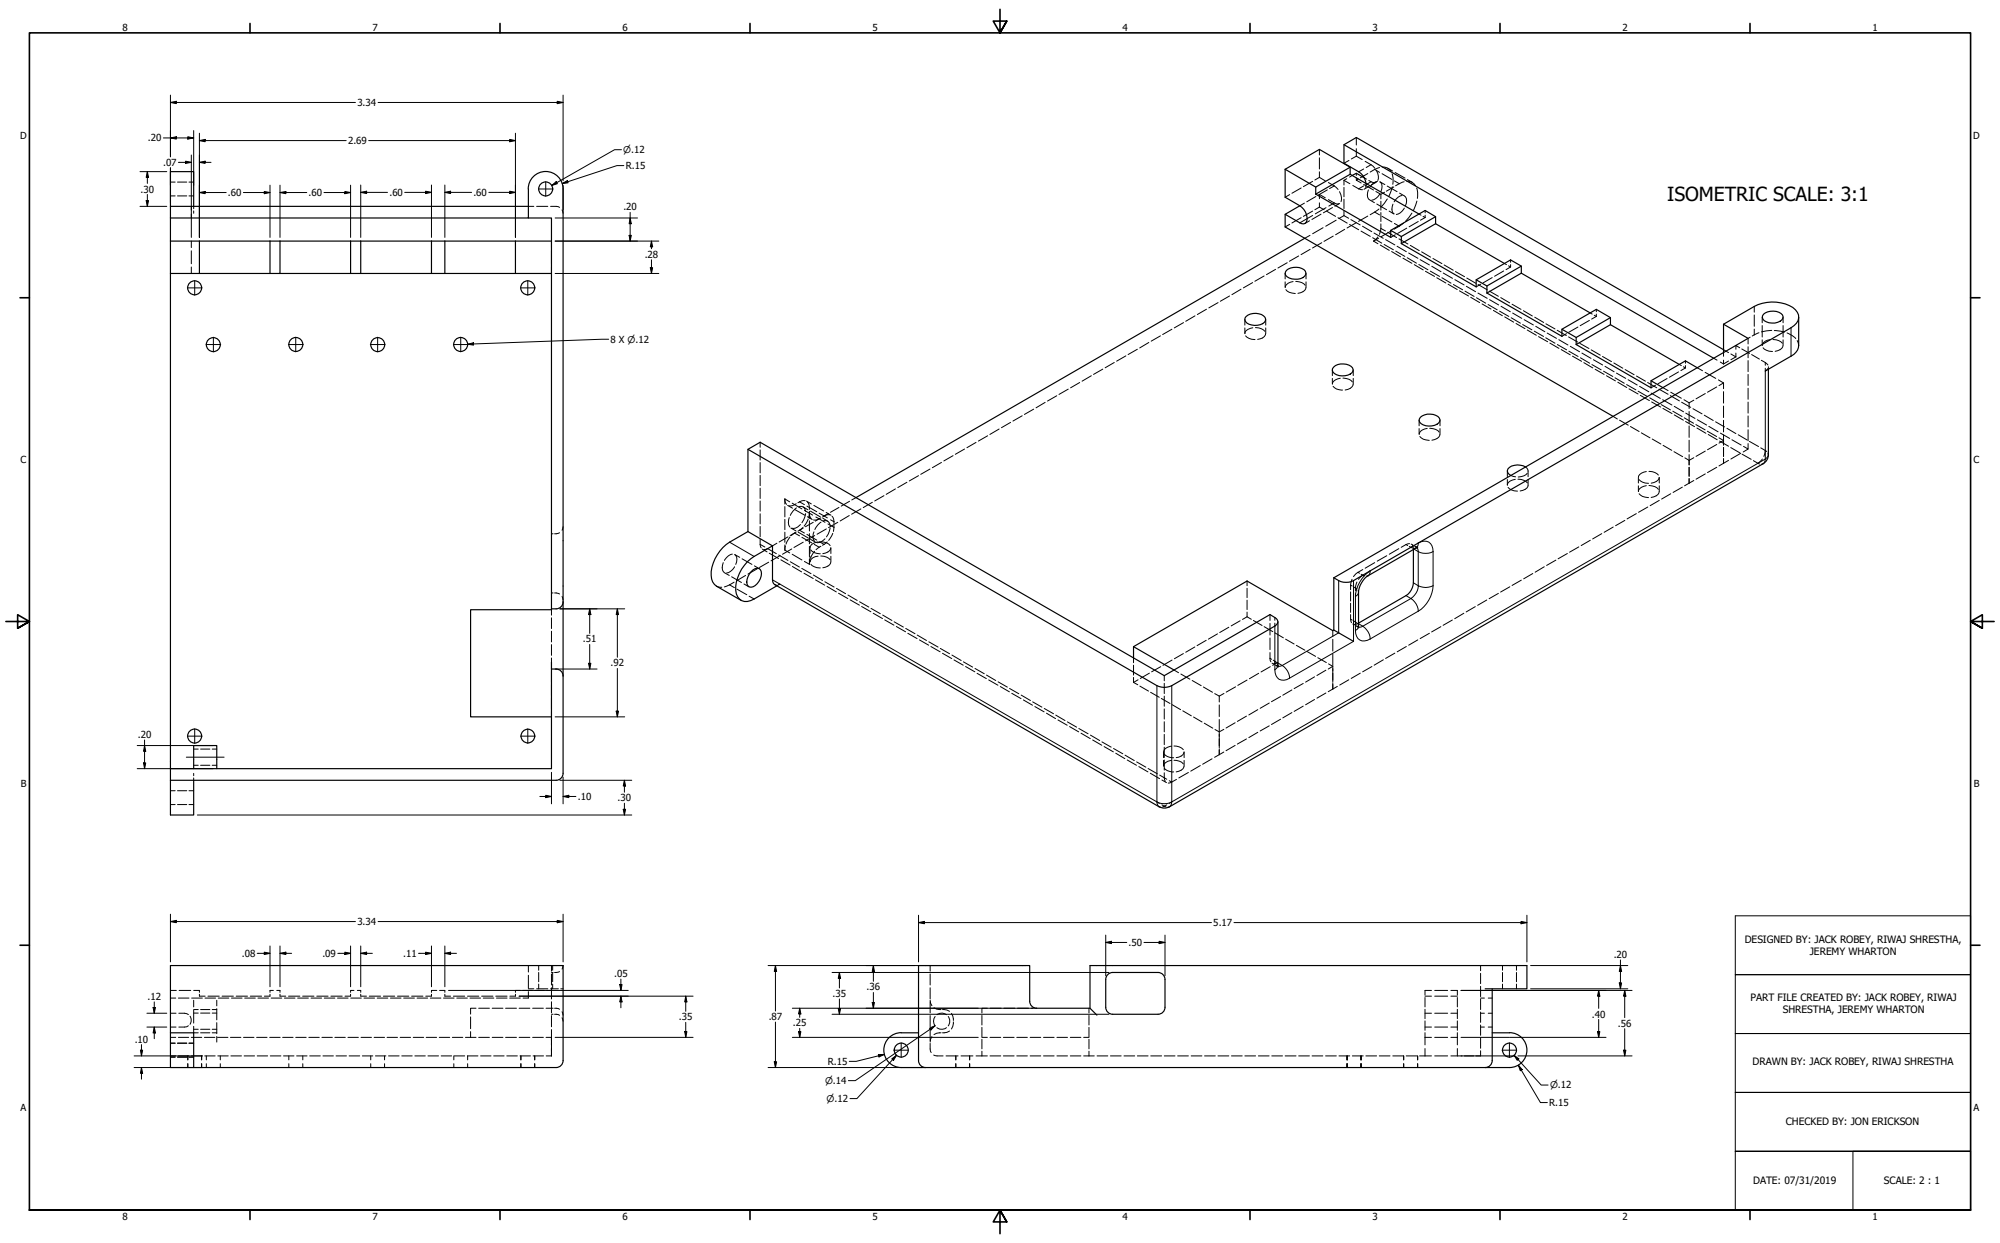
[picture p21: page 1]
SCALE: 2 : 1; DATE: 07/31/2019; JEREMY WHARTON; ISOMETRIC SCALE: 3:1

DESIGNED BY: JACK ROBEY, RIWAJ SHRESTHA,

PART FILE CREATED BY: JACK ROBEY, RIWAJ

SHRESTHA, JEREMY WHARTON

DRAWN BY: JACK ROBEY, RIWAJ SHRESTHA

CHECKED BY: JON ERICKSON

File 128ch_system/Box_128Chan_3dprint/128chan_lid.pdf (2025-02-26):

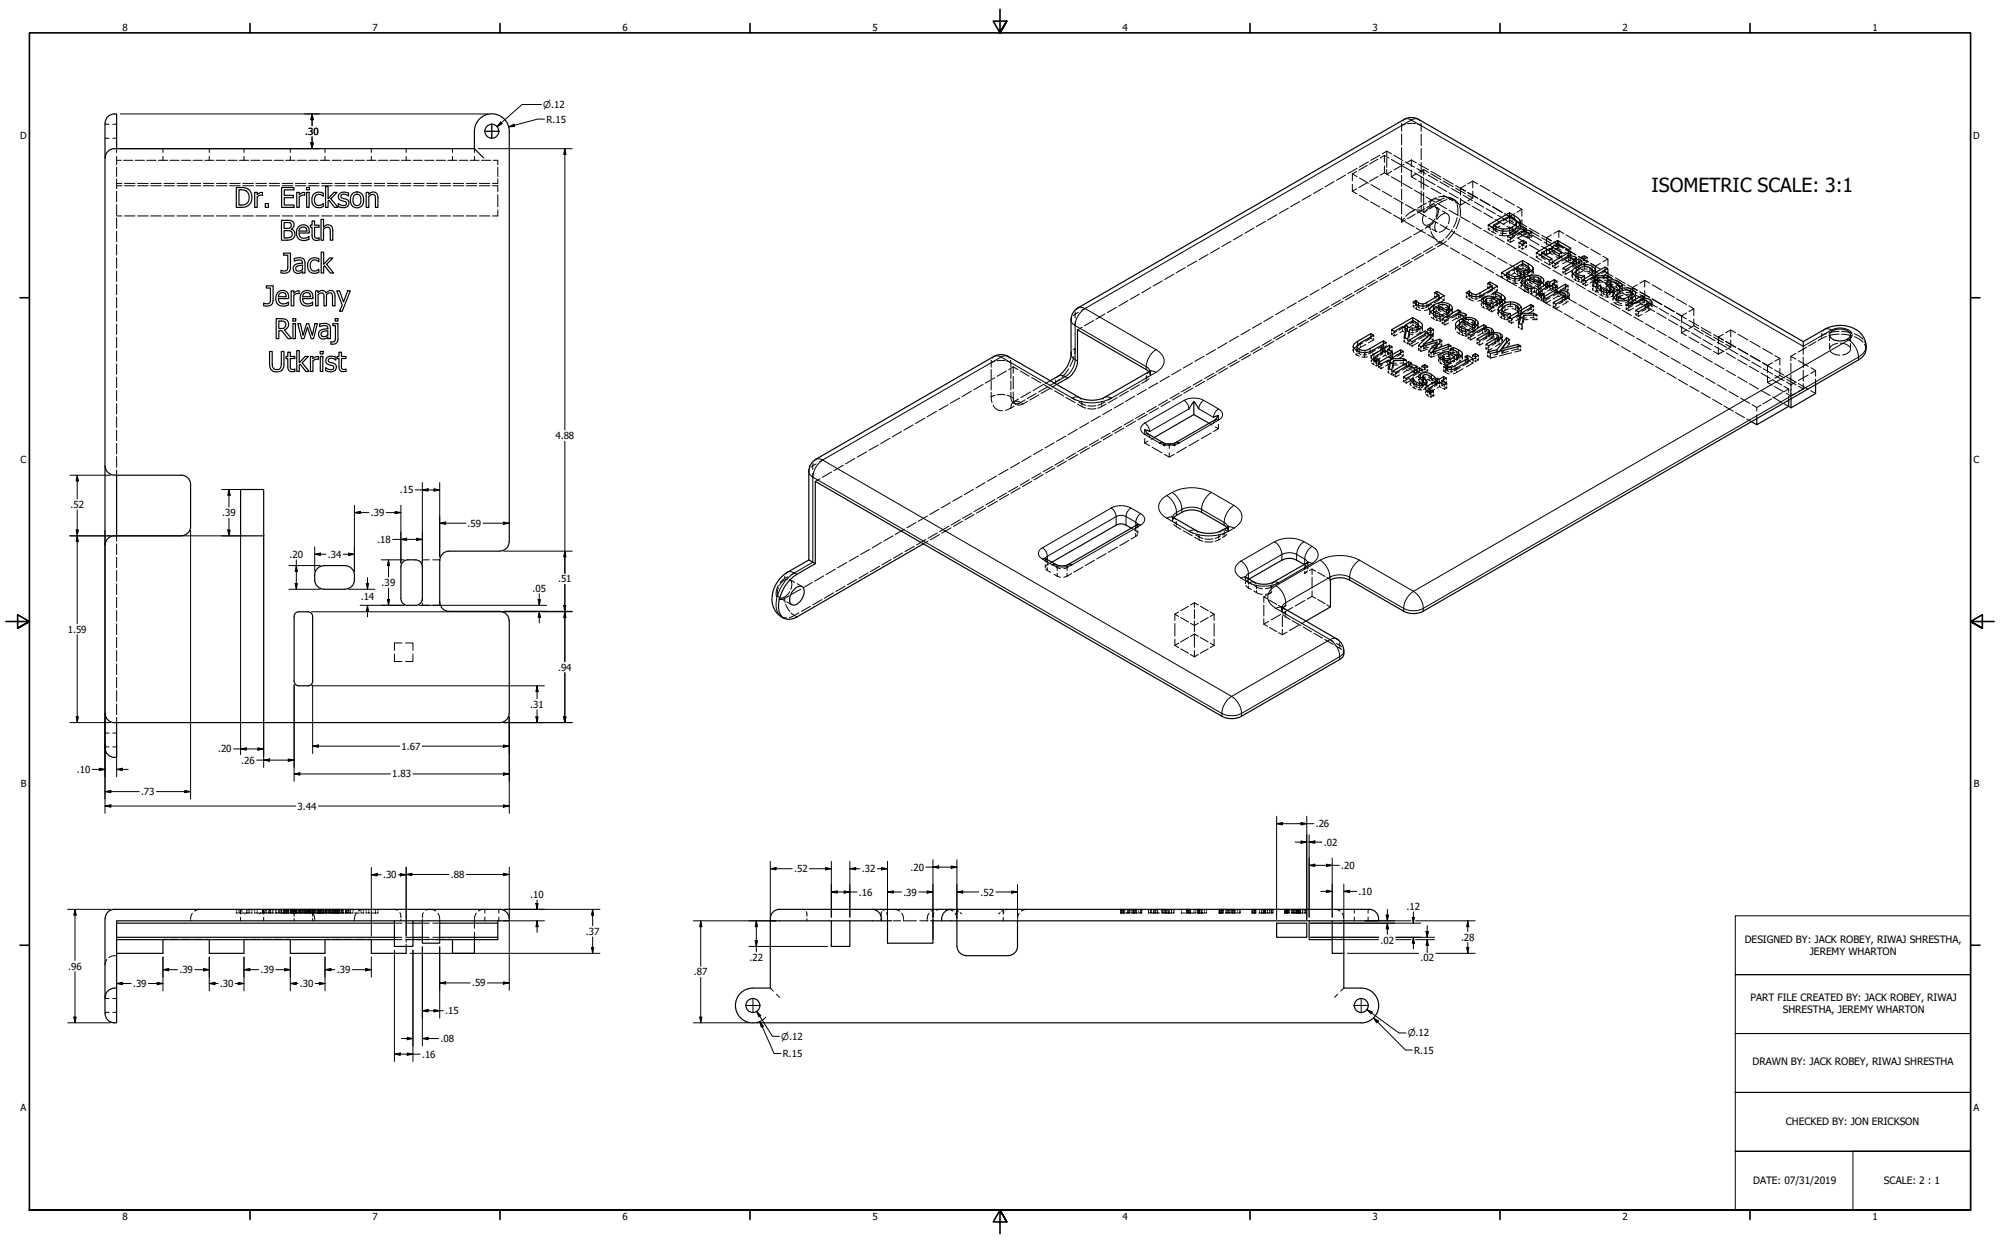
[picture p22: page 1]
ISOMETRIC SCALE: 3:1; SCALE: 2 : 1; DATE: 07/31/2019; JEREMY WHARTON

DESIGNED BY: JACK ROBEY, RIWAJ SHRESTHA,

PART FILE CREATED BY: JACK ROBEY, RIWAJ

SHRESTHA, JEREMY WHARTON

DRAWN BY: JACK ROBEY, RIWAJ SHRESTHA

CHECKED BY: JON ERICKSON

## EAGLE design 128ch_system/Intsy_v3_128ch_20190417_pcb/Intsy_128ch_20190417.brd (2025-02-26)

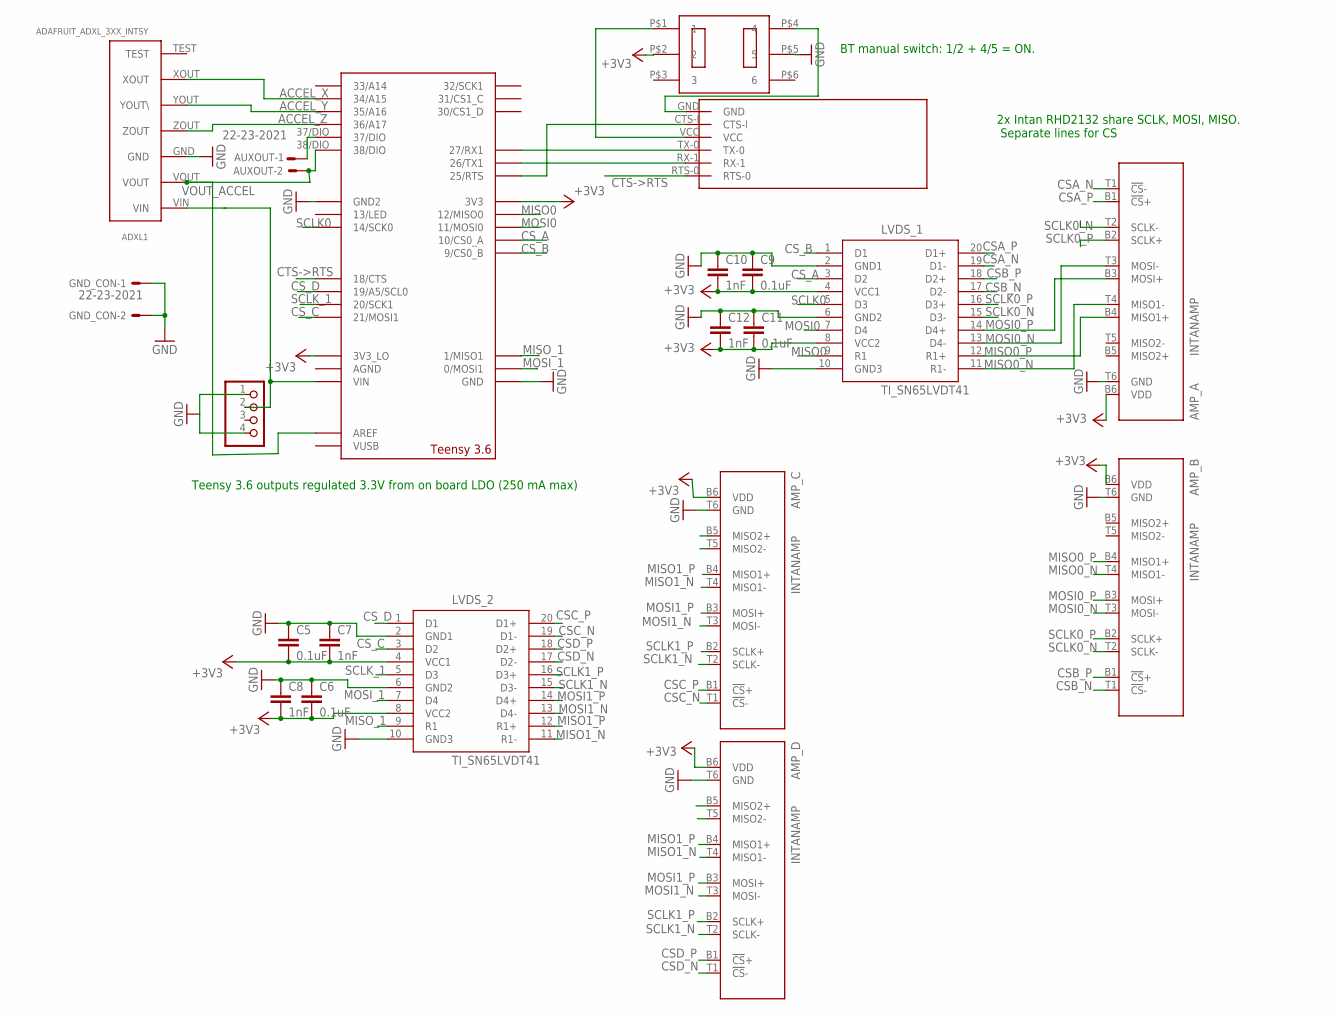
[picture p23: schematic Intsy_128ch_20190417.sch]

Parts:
ADXL1: ADAFRUIT_ADXL_3XX_INTSY; ADAFRUIT_ADXL_3XX
AMP_A: INTANAMP; AMPBOARD
AMP_B: INTANAMP; AMPBOARD
AMP_C: INTANAMP; AMPBOARD
AMP_D: INTANAMP; AMPBOARD
AUXOUT: 22-23-2021
C5, C6, C9, C11: 0.1uF; C2012
C7, C8, C10, C12: 1nF; C2012
DPDT_1: DPDT_1; SLIDE_SWITCH_DPDT_NIDEC
GND_CON: 22-23-2021
LVDS_1, LVDS_2: TI_SN65LVDT41; SN65LVDT41_TSSOP20
RN42: RN42
SW1: LiPoIn; PADS-4
U$2: TEENSY_3.5/3.6_SIMPLE

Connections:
+3V3: AMP_A.B6 (VDD), AMP_B.B6 (VDD), AMP_C.B6 (VDD), AMP_D.B6 (VDD), C5.2, C6.2, C7.2, C8.2, C9.2, C10.2, C11.2, C12.2, DPDT_1.P$2 (2), LVDS_1.4 (VCC1), LVDS_1.8 (VCC2), LVDS_2.4 (VCC1), LVDS_2.8 (VCC2), U$2.3V3, U$2.3V3_LO
ACCEL_X: ADXL1.XOUT, U$2.34/A15
ACCEL_Y: ADXL1.YOUT (YOUT\), U$2.35/A16
ACCEL_Z: ADXL1.ZOUT, U$2.36/A17
CSA_N: AMP_A.T1 (!CS!-), LVDS_1.19 (D1-)
CSA_P: AMP_A.B1 (!CS!+), LVDS_1.20 (D1+)
CSB_N: AMP_B.T1 (!CS!-), LVDS_1.17 (D2-)
CSB_P: AMP_B.B1 (!CS!+), LVDS_1.18 (D2+)
CSC_N: AMP_C.T1 (!CS!-), LVDS_2.19 (D1-)
CSC_P: AMP_C.B1 (!CS!+), LVDS_2.20 (D1+)
CSD_N: AMP_D.T1 (!CS!-), LVDS_2.17 (D2-)
CSD_P: AMP_D.B1 (!CS!+), LVDS_2.18 (D2+)
CS_A: LVDS_1.3 (D2), U$2.10/CS (10/CS0_A)
CS_B: LVDS_1.1 (D1), U$2.9/CS (9/CS0_B)
CS_C: LVDS_2.3 (D2), U$2.21/CS0/MOSI1 (21/MOSI1)
CS_D: LVDS_2.1 (D1), U$2.19/A5/SCL (19/A5/SCL0)
CTS->RTS: RN42.RTS-0, U$2.18/CTS
GND: ADXL1.GND, AMP_A.T6 (GND), AMP_B.T6 (GND), AMP_C.T6 (GND), AMP_D.T6 (GND), C5.1, C6.1, C7.1, C8.1, C9.1, C10.1, C11.1, C12.1, DPDT_1.P$5 (5), GND_CON.1, GND_CON.2, LVDS_1.2 (GND1), LVDS_1.6 (GND2), LVDS_1.10 (GND3), LVDS_2.2 (GND1), LVDS_2.6 (GND2), LVDS_2.10 (GND3), SW1.1, SW1.4, U$2.GND, U$2.GND2
MISO0: LVDS_1.9 (R1), U$2.12/MISO0
MISO0_N: AMP_A.T4 (MISO1-), AMP_B.T4 (MISO1-), LVDS_1.11 (R1-)
MISO0_P: AMP_A.B4 (MISO1+), AMP_B.B4 (MISO1+), LVDS_1.12 (R1+)
MISO1_N: AMP_C.T4 (MISO1-), AMP_D.T4 (MISO1-), LVDS_2.11 (R1-)
MISO1_P: AMP_C.B4 (MISO1+), AMP_D.B4 (MISO1+), LVDS_2.12 (R1+)
MISO_1: LVDS_2.9 (R1), U$2.1/MISO1
MOSI0: LVDS_1.7 (D4), U$2.11/MOSI0
MOSI0_N: AMP_A.T3 (MOSI-), AMP_B.T3 (MOSI-), LVDS_1.13 (D4-)
MOSI0_P: AMP_A.B3 (MOSI+), AMP_B.B3 (MOSI+), LVDS_1.14 (D4+)
MOSI1_N: AMP_C.T3 (MOSI-), AMP_D.T3 (MOSI-), LVDS_2.13 (D4-)
MOSI1_P: AMP_C.B3 (MOSI+), AMP_D.B3 (MOSI+), LVDS_2.14 (D4+)
MOSI_1: LVDS_2.7 (D4), U$2.0/MOSI1
unnamed: ADXL1.VIN, SW1.2, U$2.VIN
unnamed: AUXOUT.1, U$2.37/DIO
unnamed: DPDT_1.P$4 (4), RN42.GND
unnamed: RN42.TX-0, U$2.27/RX1
unnamed: RN42.RX-1, U$2.26/TX1
unnamed: RN42.CTS-I, U$2.25/RTS
unnamed: DPDT_1.P$1 (1), RN42.VCC
SCLK0: LVDS_1.5 (D3), U$2.14/SCK0
SCLK0_N: AMP_A.T2 (SCLK-), AMP_B.T2 (SCLK-), LVDS_1.15 (D3-)
SCLK0_P: AMP_A.B2 (SCLK+), AMP_B.B2 (SCLK+), LVDS_1.16 (D3+)
SCLK1_N: AMP_C.T2 (SCLK-), AMP_D.T2 (SCLK-), LVDS_2.15 (D3-)
SCLK1_P: AMP_C.B2 (SCLK+), AMP_D.B2 (SCLK+), LVDS_2.16 (D3+)
SCLK_1: LVDS_2.5 (D3), U$2.20/CS0/SCK1 (20/SCK1)
VOUT_ACCEL: ADXL1.VOUT, AUXOUT.2, U$2.38/DIO, U$2.AREF

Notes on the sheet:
2x Intan RHD2132 share SCLK, MOSI, MISO. Separate lines for CS
Teensy 3.6 outputs regulated 3.3V from on board LDO (250 mA max)
BT manual switch: 1/2 + 4/5 = ON.

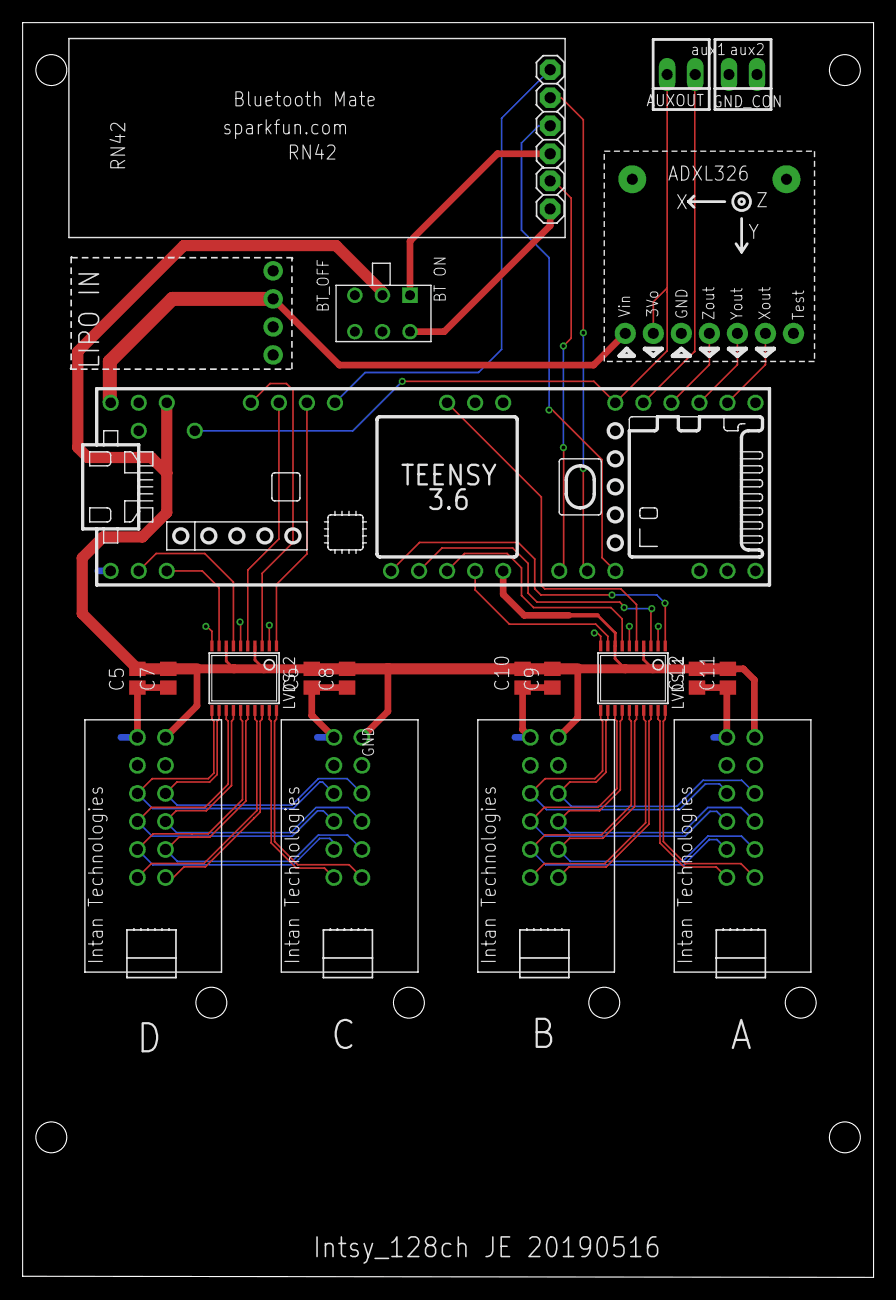
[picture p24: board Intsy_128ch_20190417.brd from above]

Board: 2 copper layers, 77.1 x 113.7 mm, 21 parts (1 on the bottom side), 44 nets.

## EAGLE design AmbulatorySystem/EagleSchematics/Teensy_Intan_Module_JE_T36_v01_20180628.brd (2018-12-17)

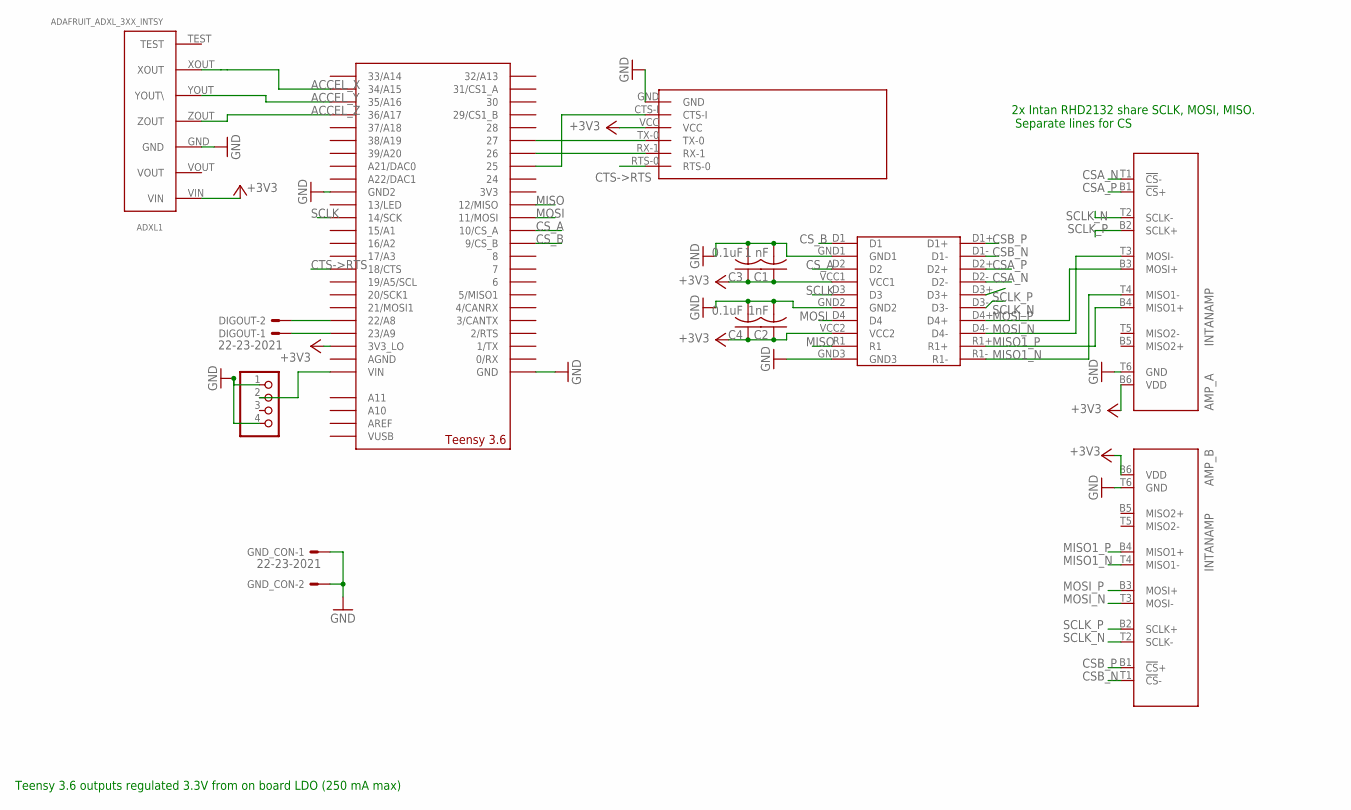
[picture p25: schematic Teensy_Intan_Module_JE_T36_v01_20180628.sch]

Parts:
ADXL1: ADAFRUIT_ADXL_3XX_INTSY; ADAFRUIT_ADXL_3XX
AMP_A: INTANAMP; AMPBOARD
AMP_B: INTANAMP; AMPBOARD
C1: 1 nF; C025-024X044
C2: 1nF; C025-024X044
C3, C4: 0.1uF; C025-024X044
DIGOUT: 22-23-2021
GND_CON: 22-23-2021
RN42: RN42
SW1: LiPoIn; PADS-4
U$1: SCHMARTBOARD20PIN
U$2: TEENSY_3.5/3.6_BASIC

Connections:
+3V3: ADXL1.VIN, AMP_A.B6 (VDD), AMP_B.B6 (VDD), C1.1, C2.1, C3.1, C4.1, RN42.VCC, U$1.VCC1, U$1.VCC2, U$2.3V3_LO
ACCEL_X: ADXL1.XOUT, U$2.34/A15
ACCEL_Y: ADXL1.YOUT (YOUT\), U$2.35/A16
ACCEL_Z: ADXL1.ZOUT, U$2.36/A17
CSA_N: AMP_A.T1 (!CS!-), U$1.D2-
CSA_P: AMP_A.B1 (!CS!+), U$1.D2+
CSB_N: AMP_B.T1 (!CS!-), U$1.D1-
CSB_P: AMP_B.B1 (!CS!+), U$1.D1+
CS_A: U$1.D2, U$2.10/CS (10/CS_A)
CS_B: U$1.D1, U$2.9/CS (9/CS_B)
CTS->RTS: RN42.RTS-0, U$2.18/A4/SDA (18/CTS)
GND: ADXL1.GND, AMP_A.T6 (GND), AMP_B.T6 (GND), C1.2, C2.2, C3.2, C4.2, GND_CON.1, GND_CON.2, RN42.GND, SW1.1, SW1.4, U$1.GND1, U$1.GND2, U$1.GND3, U$2.GND, U$2.GND2
MISO: U$1.R1, U$2.12/MISO
MISO1_N: AMP_A.T4 (MISO1-), AMP_B.T4 (MISO1-), U$1.R1-
MISO1_P: AMP_A.B4 (MISO1+), AMP_B.B4 (MISO1+), U$1.R1+
MOSI: U$1.D4, U$2.11/MOSI
MOSI_N: AMP_A.T3 (MOSI-), AMP_B.T3 (MOSI-), U$1.D4-
MOSI_P: AMP_A.B3 (MOSI+), AMP_B.B3 (MOSI+), U$1.D4+
unnamed: SW1.2, U$2.VIN
unnamed: DIGOUT.2, U$2.22/A8
unnamed: DIGOUT.1, U$2.23/A9
unnamed: RN42.TX-0, U$2.27
unnamed: RN42.RX-1, U$2.26
unnamed: RN42.CTS-I, U$2.25
SCLK: U$1.D3, U$2.14/A0 (14/SCK)
SCLK_N: AMP_A.T2 (SCLK-), AMP_B.T2 (SCLK-), U$1.D3-
SCLK_P: AMP_A.B2 (SCLK+), AMP_B.B2 (SCLK+), U$1.D3+

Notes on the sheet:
2x Intan RHD2132 share SCLK, MOSI, MISO. Separate lines for CS
Teensy 3.6 outputs regulated 3.3V from on board LDO (250 mA max)

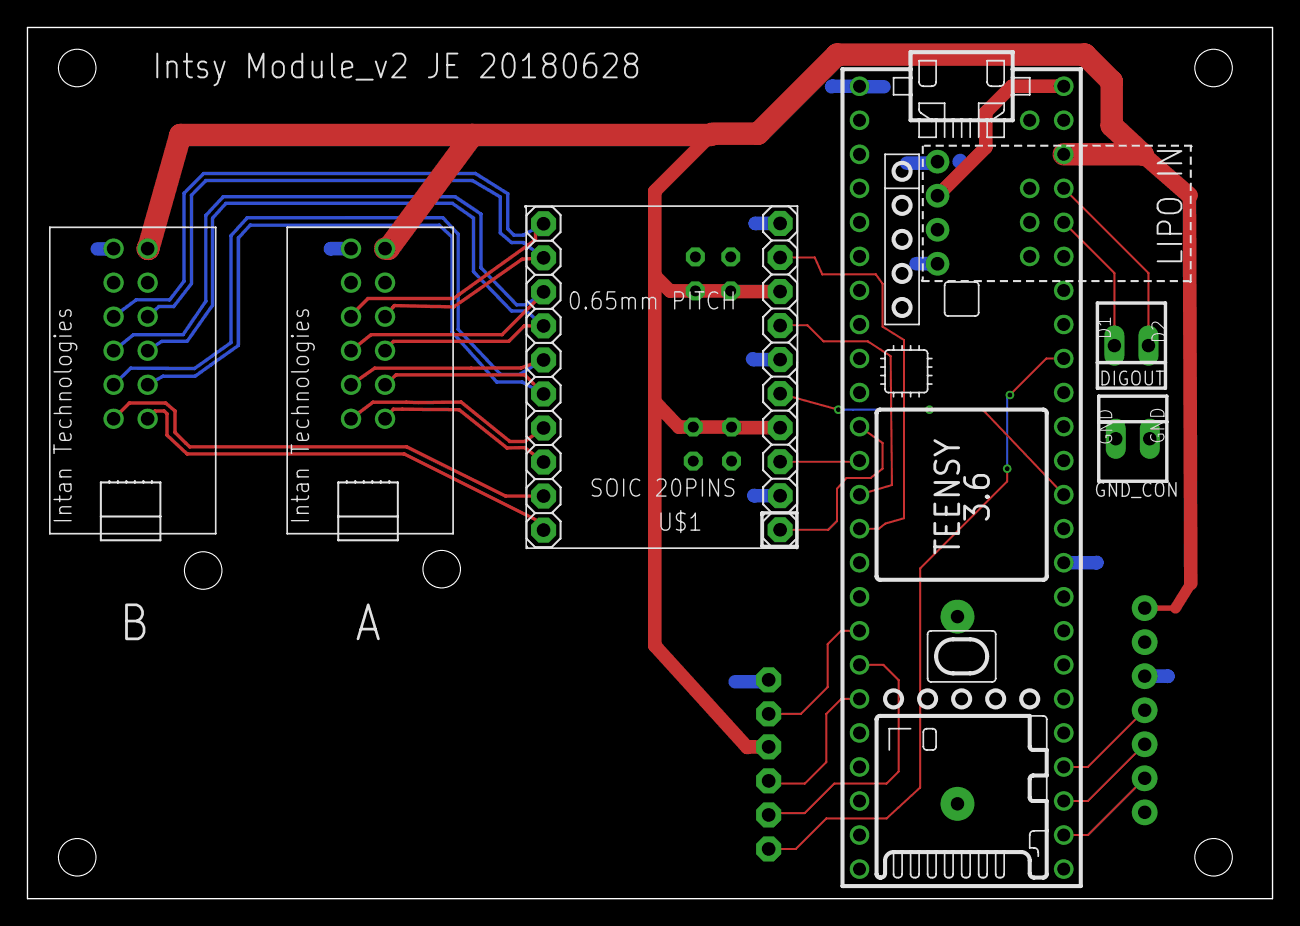
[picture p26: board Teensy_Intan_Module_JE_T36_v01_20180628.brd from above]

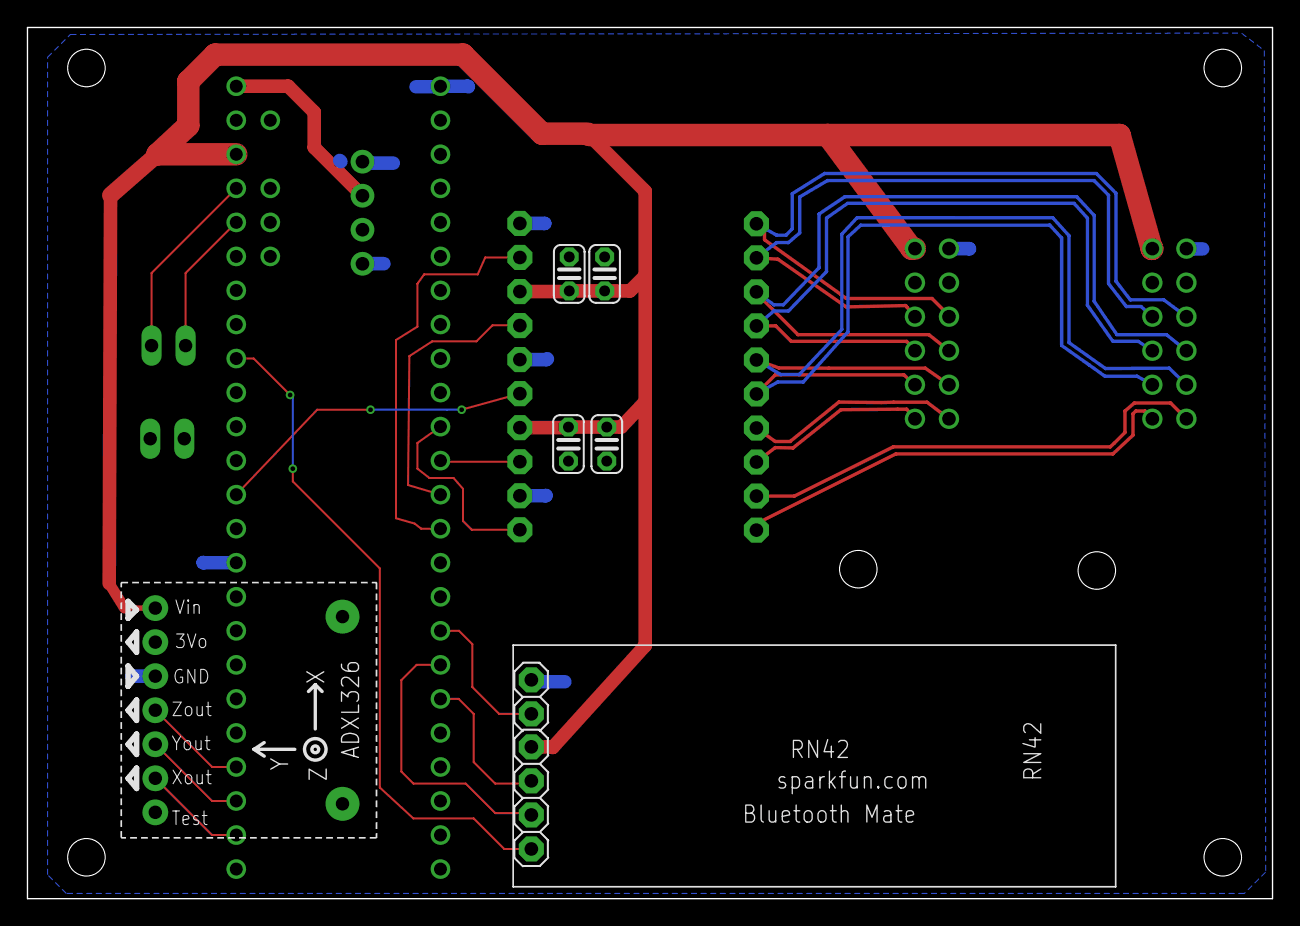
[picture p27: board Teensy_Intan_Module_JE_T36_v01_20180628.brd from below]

Board: 2 copper layers, 92.9 x 65.0 mm, 13 parts (6 on the bottom side), 27 nets.

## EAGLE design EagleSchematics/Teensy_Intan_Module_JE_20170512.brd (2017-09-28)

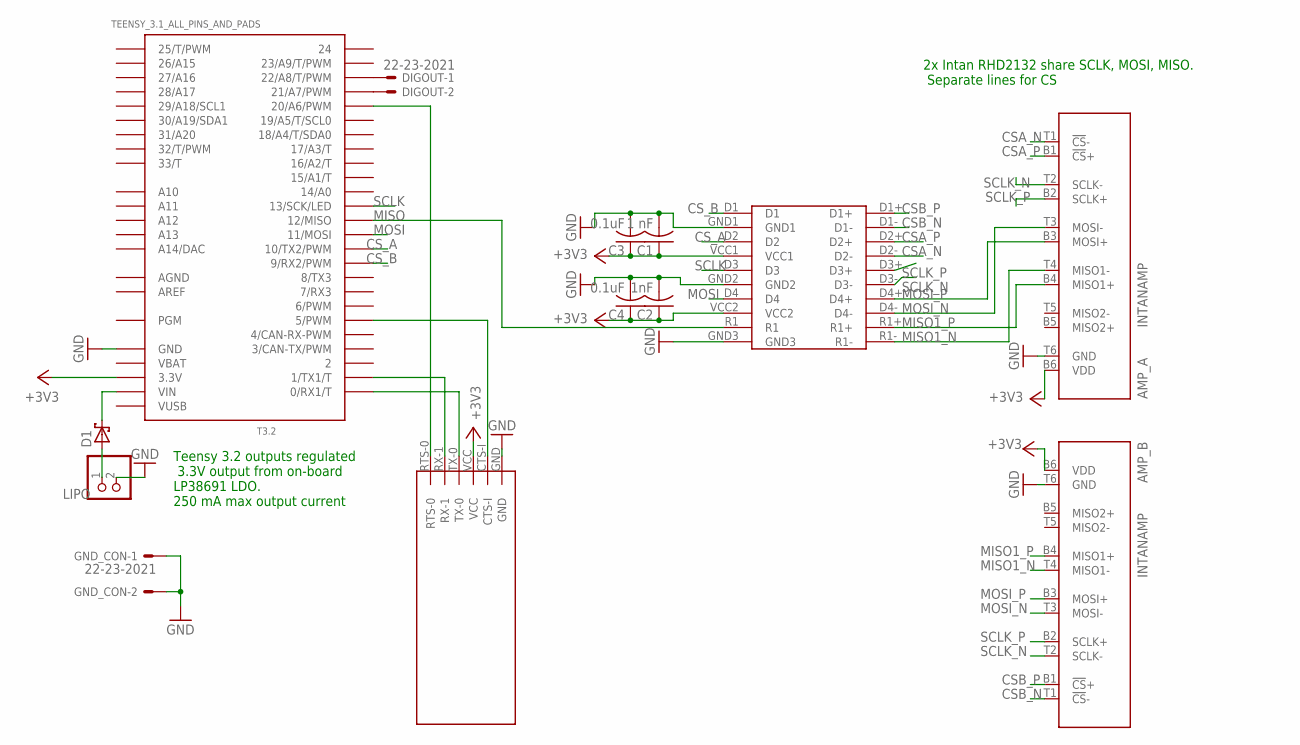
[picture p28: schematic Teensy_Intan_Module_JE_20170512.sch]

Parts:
AMP_A: INTANAMP; AMPBOARD
AMP_B: INTANAMP; AMPBOARD
C1: 1 nF; C025-024X044
C2: 1nF; C025-024X044
C3, C4: 0.1uF; C025-024X044
D1: SCHOTTKY-DIODEDO41-7; DO41-7
DIGOUT: 22-23-2021
GND_CON: 22-23-2021
LIPO: LIPO_BAT; JST-PH-2-THM
RN42: RN42
T3.2: TEENSY_3.1_ALL_PINS_AND_PADS; TEENSY_3.1_ALLPINS
U$1: SCHMARTBOARD20PIN

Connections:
+3V3: AMP_A.B6 (VDD), AMP_B.B6 (VDD), C1.1, C2.1, C3.1, C4.1, RN42.VCC, T3.2.3.3V, T3.2.3.3V1 (3.3V), T3.2.3.3V2 (3.3V), U$1.VCC1, U$1.VCC2
AGND: T3.2.AGND
AREF: T3.2.AREF
CSA_N: AMP_A.T1 (!CS!-), U$1.D2-
CSA_P: AMP_A.B1 (!CS!+), U$1.D2+
CSB_N: AMP_B.T1 (!CS!-), U$1.D1-
CSB_P: AMP_B.B1 (!CS!+), U$1.D1+
CS_A: T3.2.10 (10/TX2/PWM), U$1.D2
CS_B: T3.2.9 (9/RX2/PWM), U$1.D1
GND: AMP_A.T6 (GND), AMP_B.T6 (GND), C1.2, C2.2, C3.2, C4.2, GND_CON.1, GND_CON.2, LIPO.2 (1), RN42.GND, T3.2.GND, T3.2.GND1 (GND), T3.2.GND2 (GND), U$1.GND1, U$1.GND2, U$1.GND3
MISO: T3.2.12 (12/MISO), U$1.R1
MISO1_N: AMP_A.T4 (MISO1-), AMP_B.T4 (MISO1-), U$1.R1-
MISO1_P: AMP_A.B4 (MISO1+), AMP_B.B4 (MISO1+), U$1.R1+
MOSI: T3.2.11 (11/MOSI), U$1.D4
MOSI_N: AMP_A.T3 (MOSI-), AMP_B.T3 (MOSI-), U$1.D4-
MOSI_P: AMP_A.B3 (MOSI+), AMP_B.B3 (MOSI+), U$1.D4+
unnamed: D1.A, LIPO.1 (2)
unnamed: DIGOUT.1, T3.2.22/A8 (22/A8/T/PWM)
unnamed: DIGOUT.2, T3.2.21/A7 (21/A7/PWM)
unnamed: RN42.CTS-I, T3.2.5 (5/PWM)
unnamed: RN42.RTS-0, T3.2.20/A6 (20/A6/PWM)
RX-TN42: RN42.TX-0, T3.2.0 (0/RX1/T)
SCLK: T3.2.13 (13/SCK/LED), U$1.D3
SCLK_N: AMP_A.T2 (SCLK-), AMP_B.T2 (SCLK-), U$1.D3-
SCLK_P: AMP_A.B2 (SCLK+), AMP_B.B2 (SCLK+), U$1.D3+
TX-RN42: RN42.RX-1, T3.2.1 (1/TX1/T)
VBAT: T3.2.VBAT
VIN_LIPO: D1.C, T3.2.VIN
VUSB: T3.2.VUSB

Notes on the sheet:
2x Intan RHD2132 share SCLK, MOSI, MISO. Separate lines for CS
Teensy 3.2 outputs regulated 3.3V output from on-board LP38691 LDO. 250 mA max output current

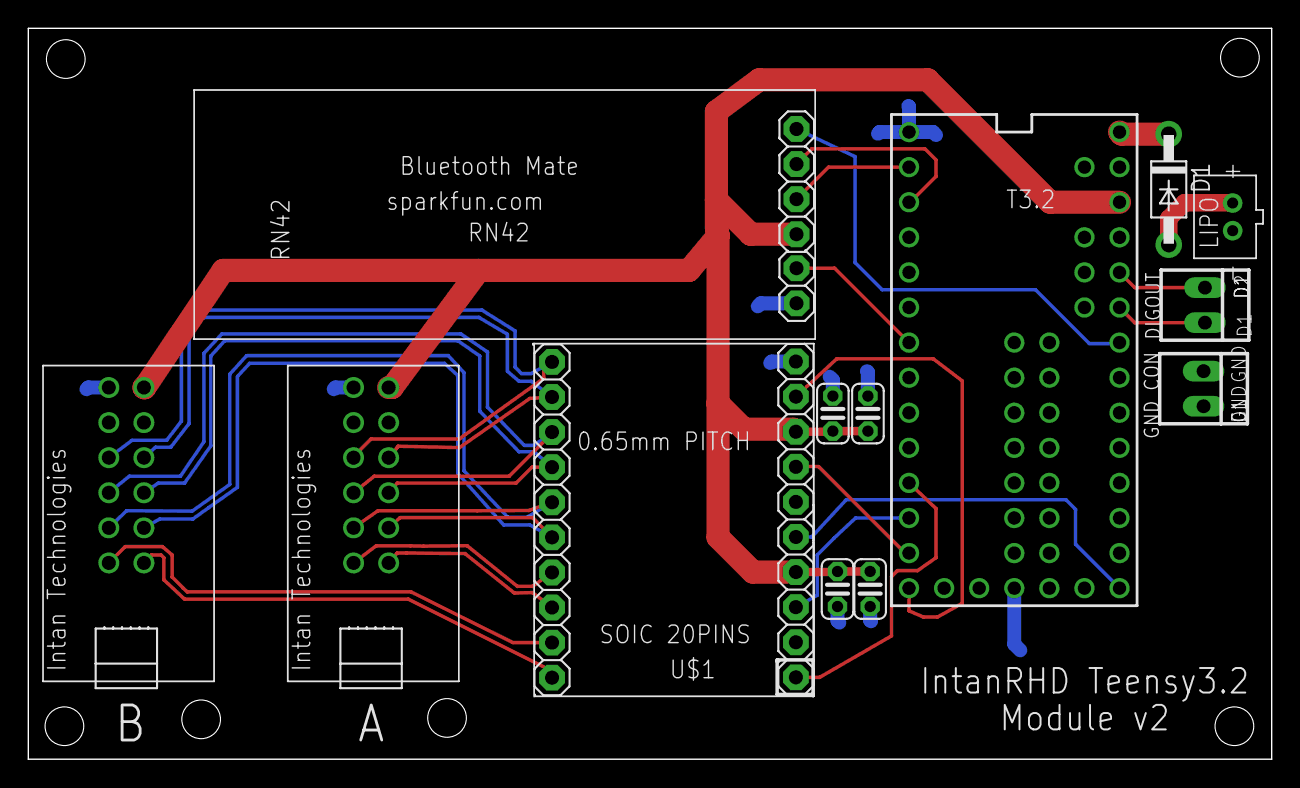
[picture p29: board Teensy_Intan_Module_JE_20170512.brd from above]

Board: 2 copper layers, 90.0 x 52.9 mm, 13 parts (0 on the bottom side), 25 nets.

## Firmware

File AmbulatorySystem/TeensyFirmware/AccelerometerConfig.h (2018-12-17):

//accelerometer pins for analog reads
const int PIN_ACCEL_X = 34;
const int PIN_ACCEL_Y = 35;
const int PIN_ACCEL_Z = 36;
uint16_t accelX;
uint16_t accelY;
uint16_t accelZ;

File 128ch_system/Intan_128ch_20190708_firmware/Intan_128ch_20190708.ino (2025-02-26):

/*
   128 channel Intsy system with:
   Teensy 3.6 + (up to) 4x Intan RHD2132 amplifier boards + ADXL335 accelerometer + onboard microSD logging capabiilty
   Developed by: Jon Erickson, Washington and Lee University, Dept of Physics and Engineering
   Contact: ericksonj@wlu.edu

  Revision History:

  JE 09 Jan 2020:   - temp change A18 to A21 for TTL direct measurement. A18 measures on-board flex sensor via voltage divider
  JE 08 July 2019:  - adding support for another analog input, intended to be flex sensor readings for Intsy system

  JE 24 June 2019:  - various updates complete to serial streaming selected subset of channels now complete
                    - enable measure Vdd on Intan amp A 
                    - add hello blink indicating serial ports are connected, LED blinks 10 times fast (100 ms on/off intervals)


  JE 04 June 2019:  - Adding (up to) 128 channel capabilty (amps C and D)
                    - Improved control of realtime data streaming for visualizating subsets of channels
                      Data is *always* logged to SD, unless log file is finished
                    
                    - Autodetect number of amplifiers
                    - Leaner/faster writing to SD (maybe later?)
                    - June 08 2019: update serial stream channels only at beginning of data frame.



  JE 16 Dec 2018:   - Significant updates to SD logging complete.  Using pre-allocated, pre-erased file to minimize SD write latency.
                      SD logging requires downloading Bill Greiman's SdFat libarary for Teensy: https://github.com/greiman/SdFat)
                      (Massive thanks to Bill for making this library freely available!)
                      Sd logging tests completed using fs = 100 Hz and 500 Hz; data sync and SD writes were observed to have 100% fidelity (no missing bits, no miswrites)
                      Recommend using modern/high-end SD card for minimizing latency. Tests in the Erickson lab were done using modern Samsung Evo Plus 32 GB SD card (10 bucks from BestBuy)
                    - Streaming to UART serial max streaming rate is enforced to 50 Hz x 64 chans or 100 Hz x 32 chan.  These correspond to max Bluetooth 2.0 module bandwidth.
                      Subsampled data can be streamed to serial for viewing purposes.
                        Future development may allow selecting individual channels with high streaming rates.
                    - Duration of Recording/Logging (hrs) is a required user input
                    - Note: some pin assingments have changed for SPI and UART rts/cts. These have been updated appropriately
                    - This firmware is ostensibly for 64 channel device, but can be easily modified to 32 chan operation.
                       Future development may allow auto-detection of Intan RHD2000 device present/plugged into hardware port


  JE 10 July 2018:  - started development, based on Intan_LV_interface_64chan_alpha. Some pin assignments have changed moving to T3.6
                    - Major updates/upgrades include:
                      1. Streaming to microSD card (should make this optional, but for now always turned on, since this is intended for ambulatory system)
                      2. ADXL335  analaog  accelerometer measurements (x,y,z) - useful for determining motion/resting periods of test subject
                      3. Circular buffer implementation to improve robustness of ADC conversion timing in interval timer interrupts

  JE 24 Oct 2018:  -capability to stream to serial and to Sd file at different rates (has to be integer multiples).  For example, stream data to SD at 100 Hz, but stream data to PC to check signal quality at (max) 50 Hz.
                   - add 'check in' capability - serial stream can be turned on or off at will


  General Info:
  SPI interface for communicating with 2x Intan RHD2132 bioamplifier chip.
  Interrupts are used to convert ADC channels, aux cmd results, and timestamp at which conversion starts
  Serial data is written to Serial port (USB or UART) once data stream starts. Intan data streams are also written to SD card, along with accelerometer readings.
  Serial Port can be either USB serial or UART/Bluetooth with CTS/RTS flow control enabled.


  Character inputs control triggering of events to validate SPI interface, config registers, set filter limits, set sampling period, start and stop data acquisition, etc.

  Companion LabView front-end provides real-time visualization similar to Biosemi ActiveView system.
  See: Intan_mainControlPanel_64chan_ambulatory_v02.vi (also written by JE and availble on github site).
  Termination characters are sent to help sync LabView to the Teensy.

  Additionally, 2 digital outputs are available on the Teensy, pins 21 and 22.  These may be used for digital triggers.  Currently, a short train of pulses is output on pin 22
  at the start and stop of data acquisition.  The ISR for converting ADC data turns on immediately after the falling edge of the last of 3 pulses output on pin 22.  Stopping
  the ISR for data acquisition is signaled for 5 short pulses (first rising edge signifies end of ADC conversion).

  This software is covered by the MIT license.  See below for details.

  Copyright (c) 2017 - 2018  Jonathan C Erickson

  Permission is hereby granted, free of charge, to any person obtaining a copy of this software and associated documentation files (the "Software"), to deal in the Software without restriction,
  including without limitation the rights to use, copy, modify, merge, publish, distribute, sublicense, and/or sell copies of the Software, and to permit persons to whom the Software is furnished to do so,
  subject to the following conditions:

  The above copyright notice and this permission notice shall be included in all copies or substantial portions of the Software.

  THE SOFTWARE IS PROVIDED "AS IS", WITHOUT WARRANTY OF ANY KIND, EXPRESS OR IMPLIED, INCLUDING BUT NOT LIMITED TO THE WARRANTIES OF MERCHANTABILITY, FITNESS FOR A PARTICULAR PURPOSE AND NONINFRINGEMENT.
  IN NO EVENT SHALL THE AUTHORS OR COPYRIGHT HOLDERS BE LIABLE FOR ANY CLAIM, DAMAGES OR OTHER LIABILITY, WHETHER IN AN ACTION OF CONTRACT, TORT OR OTHERWISE, ARISING FROM,
  OUT OF OR IN CONNECTION WITH THE SOFTWARE OR THE USE OR OTHER DEALINGS IN THE SOFTWARE.
*/




#include <stdlib.h>
#include <SPI.h>
#include <SdFat.h>  //requires Bill Greiman's sdFat library (downloaded July 2018 from: https://github.com/greiman/SdFat)

#include "IntanDefaultConfig.h"    // Define various 
#include "SPIconfig.h"             // Define SPI hardware pins on Teensy
#include "IntanCmd.h"              // Intan commands for read, write, calibrate, convert
#include "FilterSettingDefaults.h" // Define default Intan bandpass setting, as well as easy options
#include "setSamplingPeriod.h"     // Define sampling period for interval timer object (for Teensyduino interrupts)
#include "TeensyRestartCmd.h"      // JE don't need this since we can use _restart_Teensy() instead
#include "AccelerometerConfig.h"    // Define acceleromter pins and variables that store readings
#include "CircularBufferConfig.h"  // Define circular buffer. This is crucial element to control data flow
#include "SDwrite.h"               // setting up SD card for writing data
#include "SetStreamChannels.h"     // select subset of channels to stream over serial for real time visualization

const uint16_t INTSY_MAGIC_NUM = 0x2121;  // 'magic' number used as sync bytes to verify Teensy/SD card function (this is !! in ASCII)
const byte TERM_CHAR = 4;          //termination character, used to sync with Labview R/W.  4 = EOT = end of transmission in ASCII

// JE 08 July 2019: now using this pin to measure flex sensor reading, no output of digital pulse start
//const int DIG_OUT_START_PULSE = 37;  // output digital pulses on pin 3 to signal start of data acq


IntervalTimer SamplingPeriodTimer;          // Create an IntervalTimer object
int SAMPLE_PERIOD_MICROS = DEFAULT_TS;     // value can be set with 'm' event below, defaults to 10000 us = 100 Hz per channel
int STREAM_SAMPLING_RATIO = 2;               // value can be set with 'm' event below.  default values will produce 50 Hz max serial stream rate.

bool DEBUG_VERBOSE = false;                //verbose debugging option, prints to serial

// ------------------------------------------
//  For autodetect-hardware config here.
//  Either Serial of Serial1 should be connected
// -------------------------------------------

Stream  *SERIALNAME;
//port will be set later according to which serial comm is live
byte initialByte;  // initial byte sent to one of the serial ports

bool SerialSetFlag = false; // serial port set?   initialize start false
// then turn true once we detect a byte at one of the ports

bool StreamToSerial = true; // flag to stream data to serial or not.  Used in loop() to stream data to serial (or not).




const int BAUD_RATE_UART_BT =  115200; // baud rate Serial1 port, this is set equal to RN-42 baud rate (Silver Mate from Sparkfun).  Have trialed 230400 baud rate on 01 May 2017 - did not work. 115200 is the max for now.
const int BAUD_RATE_USB =  9600; // baud rate Serial port, only affects UART, not USB which always runs at 12 MB/s, see: https://www.pjrc.com/teensy/td_serial.html

const int RTS_TEENSY = 25;  //for RTS/CTS hardware flow control pins for UART RN-42 bluetooth
const int CTS_TEENSY = 18;
const int RX_PIN_TEENSY = 27;  // set Rx/Tx pin numbers for UART RN-42 bluetooth comms (over Serial1)
const int TX_PIN_TEENSY = 26;

const int NUM_ADC_BITS_TEENSY = 16;  // Set resolution of Teensy analog reads.
// Note: Teensy3.6 has native 13 bit resolution.
// 16 bits (=2 bytes) is convenient for file format but doesn't offer any additional resolution



// ------------------------------------------
//  Declare some variables, used later. Voltatile is needed for interrupts to do A/D conversion with convert() cmd
// -------------------------------------------

const unsigned int SPI_PIPE_DELAY = 2; //Intan's results return 2 commands later in SPI command pipe.

int numAmpsVerified;                              // value returns for SPIgetAmplInfo.  Should be either integer multiple of 32x (or 0 if error).
// could use in future to determine which amps are connected



// byte adcbytes [NUM_BYTES_PER_SCAN];           // allocate memory to copy adcbytes for serial.write();
// JE 19 June 2017. this is declared below in loop().  faster to declare here so we don't have to keep allocating over and over?


unsigned int Navail;
unsigned int NumTx;

uint16_t throwAwayRead;  //place holders for 2 delay in SPI command: throw away data

int serialID;  // USB or UART serial port connected? 0 = Serial (USB); 1 = Serial1 (UART)



// -------------------------------------------------------------------------------
//  SETUP:  start serial port, and initialize and verify SPI interface only (JE 1 Dec 2016)
// -------------------------------------------------------------------------------
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

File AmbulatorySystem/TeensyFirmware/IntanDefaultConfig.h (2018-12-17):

// -----------------------------------------------------------------------------
// DEFINE DEFAULT VALUES FOR WRITING INTAN RHD2132 REGISTERS
// These define various modes of operation with the chip, such as abs mode
// Note that WEAK_MISO can be set 0 if expanding to 64 channel system
// ** indicates user selectable
// -----------------------------------------------------------------------------

//configuration constants
const int NUM_AMPS_PER_CHIP =  32; //number of amplifiers with 2xRHD2132 chip. Fancier/better would be to allocate this after reading number of amps from register on-board chip
const int NUM_AUX_CMD = 2; // 2 aux commands x 2 chips.
const unsigned int NUM_BYTES_PER_SCAN = 2 * (2 * NUM_AUX_CMD  + 2 * NUM_AMPS_PER_CHIP) + 4 + 6 + 2; 
                  // 2 Intan chips * 32 adc conversion data (2 bytes each)
                  //  + 2 auxiliary cmd results (2 bytes each) 
                  // + 4 bytes for 32 bit timestamp 
                  //  + 6 (accelerometer xyz)
                  //  +1 sync word
                  // = 2x(64 + 4) + 4 + 6 + 2 = 148 bytes



// extern function declaration
extern void ConfigureRegisters_0_17();


// REG 0
const byte ADC_REF_BW = 3; // always set to 3 (see RHD2000 datasheet, page 19)
byte AMP_fast_settle = 0; //Set to 1 to enable  **
byte AMP_Vref_En = 1; // wait 100 us before ADC calibration; set to 0 to turn off this feature **
const byte ADC_comparator_bias = 3; // always set to 3 for normal operation
const byte ADC_comparator_select = 2; // always set to 2 for normal operation

// REG 1
byte ADC_BUFFER_BIAS = 32; // optimum current value. See page 27 **
byte VDD_SENSE_EN = 0; // set to 0 for no voltage supply sensor  **

// REG 2
const byte MUX_BIAS = 40; // set to 40 for <120kS/s

// REG 3
const byte MUX_LOAD = 0; // always set to 0 for normal operation (page 20)
byte TEMP_S1 = 0; // temperature sense enable   **
byte TEMP_S2 = 0; // temperature sense enable   **
byte TEMP_EN = 0; // set to 0 to disable and save power ** 
byte DIGOUT_HiZ = 1; // set to 1 for high impedance mode. **
byte DIGOUT = 0; // value driven to Aux Dig Out, if DIGOUT_HiZ = 0, set to 0 for now  **

// REG 4
const byte WEAK_MISO = 0; // set to 0 for multiple chips sharing single MISO line, when CS pulled high, MISO goes into hi Z state. (Intan RHD2000 datasheet, pg 20)
const byte TWOSCOMP = 0; // for unsigned ADC
const byte ABSMODE = 0; // set to  0 for no absolute value function on ADC
byte DSPen = 0; // 0 to disable offset removal for DSP
byte DSP_cutoff = 0; // range = 0-15; does not matter if DSPen = 0

// REG 5 **
const byte Z_DAC_PWR = 0; // 0 for no impedance testing.
const byte Z_LOAD = 0; // always 0 for normal operation
const byte Z_SCALE = 0; // not important since no Z measurement done
const byte Z_CONN_ALL = 0; //0 in normal operation
const byte Z_SEL_POL = 0; // only used for for RHD2216 to select for sign
const byte Z_EN = 0; // set to 0 for basic recovery

// REG 6 **
const byte Z_DAC = 0; // set to 0V

// REG 7 **
const byte Zcheck_SEL = 0 ; // set to 0 because Z_EN = 0

// REG 14-17 (APWR)
byte apwrRegisterAllOn = 0b11111111;

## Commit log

2017-10-01 Add files via upload
    add bill of materials. covers 32 and 64 chan
2017-11-08 Adding setup guide
    Instructions for assembly hardware module, powering the device, firmware uploading, and connecting to host PC wired or wirelessly
2018-02-13 Modified USB isolator
    Photo of modified Adafruit USB isolator + isolated DC-DC power supply for Intsy module. This module must be modified for compatibility with 3.3 V logic prior to using with Intsy system
2018-11-16 Add files via upload
    32/64-channel ambulatory module schematic and pcb lyaout. New module includes microSD card and ADXL3xx accelerometer
    [Teensy_Intan_Module_JE_T36_v01_20180628.brd, Teensy_Intan_Module_JE_T36_v01_20180628.sch]
2018-12-17 Add files via upload
    ambulatory system PCB front/back
2018-12-17 Add files via upload
    Teensy 3.6 firmware upload
2018-12-17 Create Overview.txt
    Eagle files and gerbers for board fab
2025-02-26 3d print mechanical enclosure files
    [128chan_box_2_FixedMeasurements.ipt, 128chan_box_Botton half Drawing.dwg, 128chan_lid.dwg, ENGN_128chan_box_4.stl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]
2025-02-26 added pcb files
    [Intsy_128ch_20190417.brd, Intsy_128ch_20190417.sch]

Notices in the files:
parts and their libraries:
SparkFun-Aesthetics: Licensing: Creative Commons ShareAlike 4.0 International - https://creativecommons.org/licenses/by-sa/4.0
